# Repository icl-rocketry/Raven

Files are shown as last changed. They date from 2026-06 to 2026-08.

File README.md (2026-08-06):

# Project RAVEN

Solid-state particle detector for a rocket payload. Detects cosmic radiation
throughout flight and logs each hit with altitude, to build up counting
statistics post-flight.

Built in KiCad. Mixed-signal board: the detector board reads two independent
silicon-diode detector channels and logs events. 

## How it works 

A cosmic particle hits a reverse-biased photodiode and dumps a few femtocoulombs
of charge. A charge-sensitive amplifier turns that into a ~7 mV pulse, a
comparator checks it against a tunable threshold and the output signal is processed
by a seperate Pickle Rick board. Two diodes on two independent
channels double the sensitive area without doubling the noise.

## Repository layout

The KiCad project has five schematic sheets:
Using the ICLR Board Template

| Sheet | Contents |
|-------|----------|
| Root | status LEDs, connectors, test points |
| Power Board | Three isolated rails off a ~7.4V battery: +25V bias, +5V analogue, +3.3V digital |
| Detector Board | The signal chain: diodes, charge amps, comparators (2 channels) |

## specs

- **Enclosure:** Circa 90 x 90 x 100 mm (TBD), light-tight detector housing
- **Power:** ~1.5 W from a ~7.4V battery (cell TBC)
- **Detector:** 2x BPW34 photodiodes, biased at +50V
- **Front-end:** ADA4817-1 charge amp, TLV3201 comparator, per channel
- **MCU:** ESP32-S3

## Status

Work in progress. Schematic of the detector front-end is nearly
complete; layout, bring-up, and firmware still to come.

**Outstanding before layout:**
- Confirm comparator edge polarity on the bench (rising vs falling) before
  writing interrupt firmware
- Clear all ERC

## Firmware

Firmware is set up for PlatformIO. Clone the repo and open in PlatformIO to
build and flash.

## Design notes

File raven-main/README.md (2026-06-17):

# Ricardo Board Template
This is a KiCad template including the required components for an ESP32S3 with a USB-C port, a CAN transceiver, as well as logic power input regulation. This is the bare minimum needed for boards in the ricardo ecosystem. If you have followed the [hardware library usage instructions](https://github.com/icl-rocketry/iclr-hw), the hardware libraries will automatically be added to every project started from this template.

## Usage
To use this, clone this repository in your KiCad user templates folder.

By default, this folder is:

MacOS - ```/Users/{USERNAME}/Documents/KiCad/8.0/template/```

Windows -  ```%USERPROFILE%/Documents/KiCad/8.0/template```

Linux - ```/home/{USERNAME}/.local/share/kicad/8.0/template```

Then, you will be able to access the template when making a new project in ```KiCad -> File -> New Project from Template... -> User Templates```

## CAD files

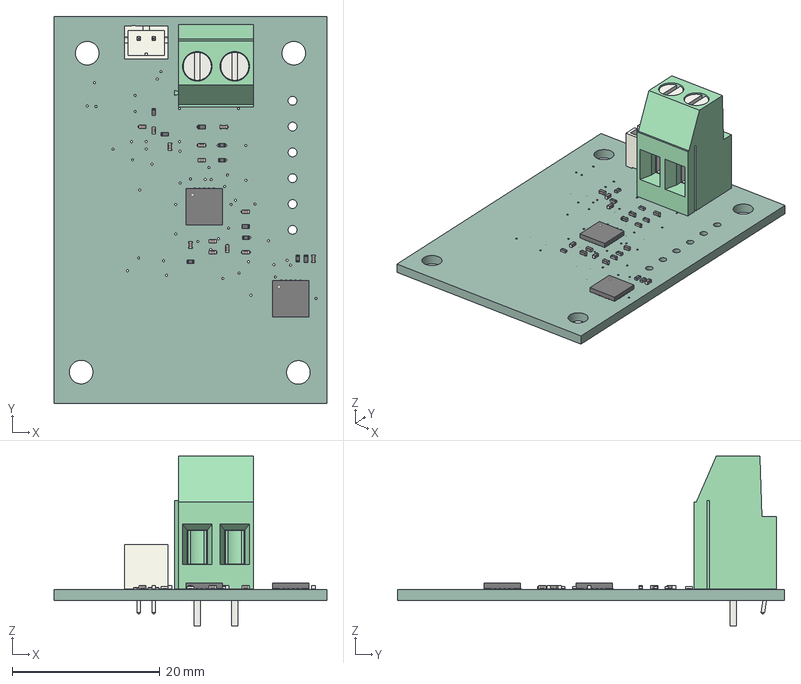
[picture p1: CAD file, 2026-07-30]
raven-main/Detector-Power-Board/Detector-Power-Board/PowerBoard.step
37.0 x 52.5 x 23.0 mm
C_0402_1005Metric x 13
R_0402_1005Metric x 10
Texas_RGW0020A_VQFN-20-1EP_5x5mm_P0.65mm_EP3.15x3.15mm x 2
JST_B2B_PH_K
TerminalBlock_Phoenix_MKDS-3-2-5.08_1x02_P5.08mm_Horizontal
det2136_PCB

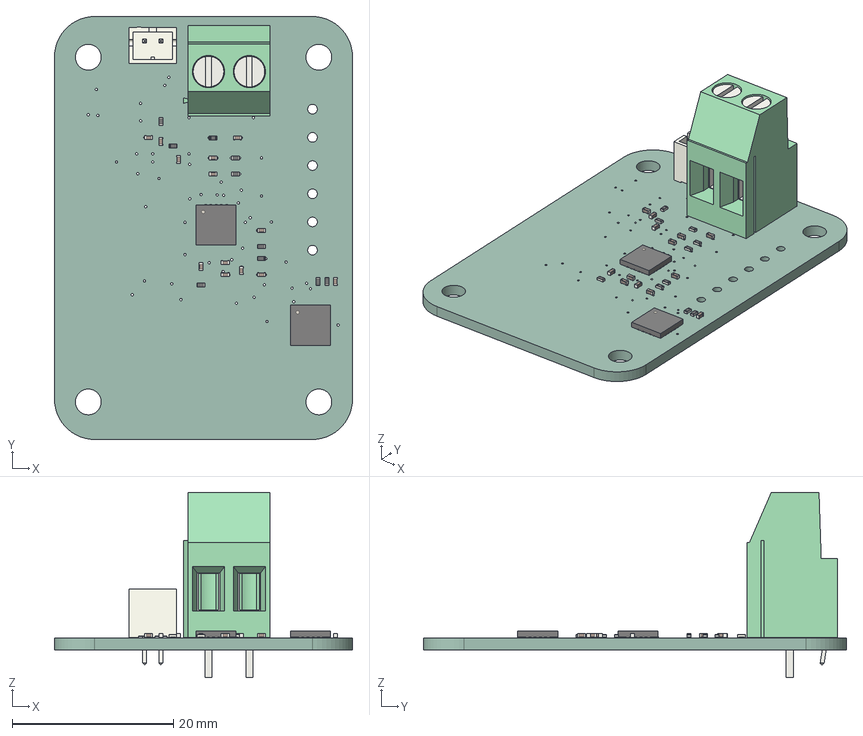
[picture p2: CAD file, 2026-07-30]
raven-main/Detector-Power-Board/PowerBoard(2).step
37.0 x 52.5 x 23.0 mm
C_0402_1005Metric x 13
R_0402_1005Metric x 10
Texas_RGW0020A_VQFN-20-1EP_5x5mm_P0.65mm_EP3.15x3.15mm x 2
JST_B2B_PH_K
TerminalBlock_Phoenix_MKDS-3-2-5.08_1x02_P5.08mm_Horizontal
detector-power_PCB

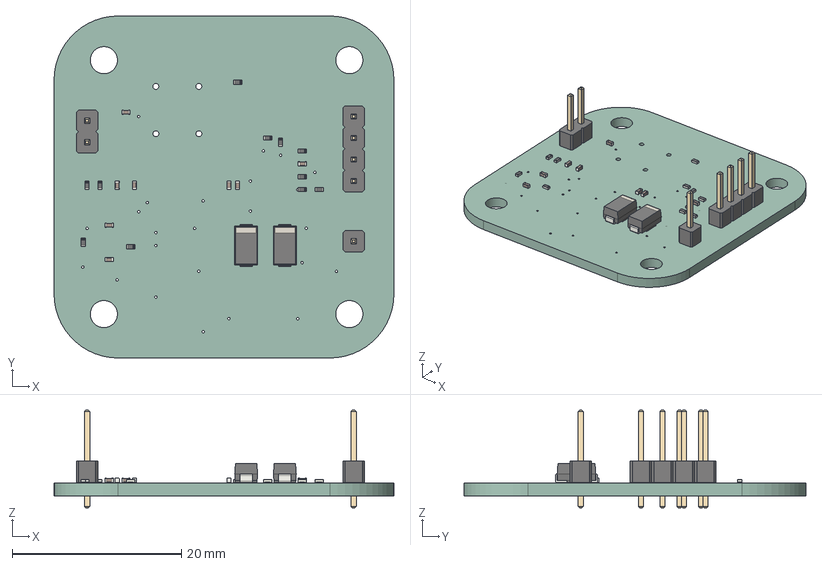
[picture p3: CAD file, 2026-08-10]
raven-main/Detector-Proto-Board/.step
40.2 x 40.4 x 11.5 mm
C_0402_1005Metric x 8
R_0402_1005Metric x 11
PinHeader_1x02_P254mm_Vertical
D_SMA x 2
PinHeader_1x01_P254mm_Vertical
PinHeader_1x04_P254mm_Vertical
Detector-Proto-Board_PCB

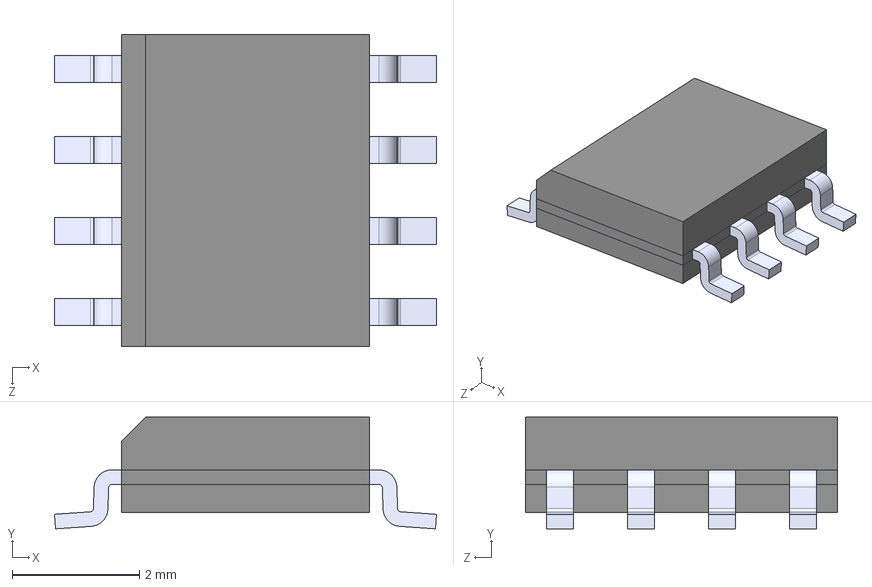
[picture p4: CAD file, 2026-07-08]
raven-main/Detector-Proto-Board/ADA4817-1ARDZ-R7/ADA4817-1ARDZ-R7.step
5.99 x 1.75 x 4.90 mm

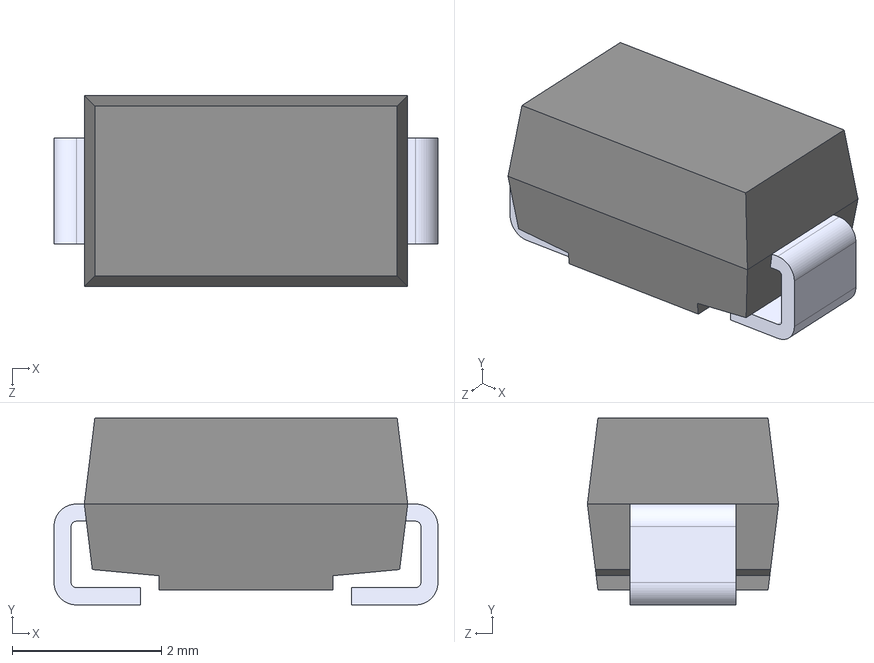
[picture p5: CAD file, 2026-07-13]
raven-main/Detector-Proto-Board/SMAJ5.0A/SMAJ5.0A.step
5.14 x 2.50 x 2.56 mm

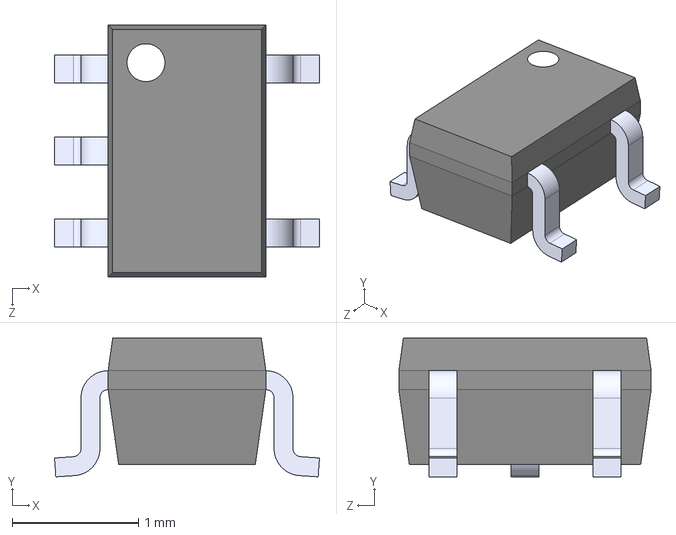
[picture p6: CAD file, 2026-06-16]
raven-main/Detector-Proto-Board/TLV3201AIDCKT/TLV3201AIDCKT.step
2.10 x 1.10 x 2.00 mm

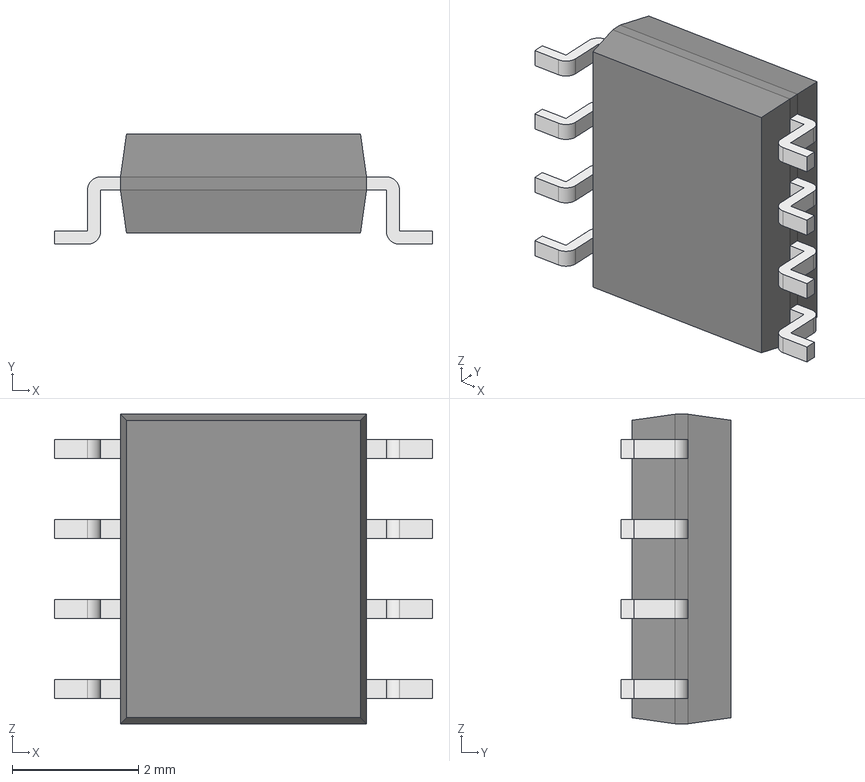
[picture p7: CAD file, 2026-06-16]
raven-main/OPA656UB/OPA656UB.step
5.99 x 1.75 x 4.91 mm
Body001 (Mirror #1) x 4
XY-plane x 12
X-axis x 12

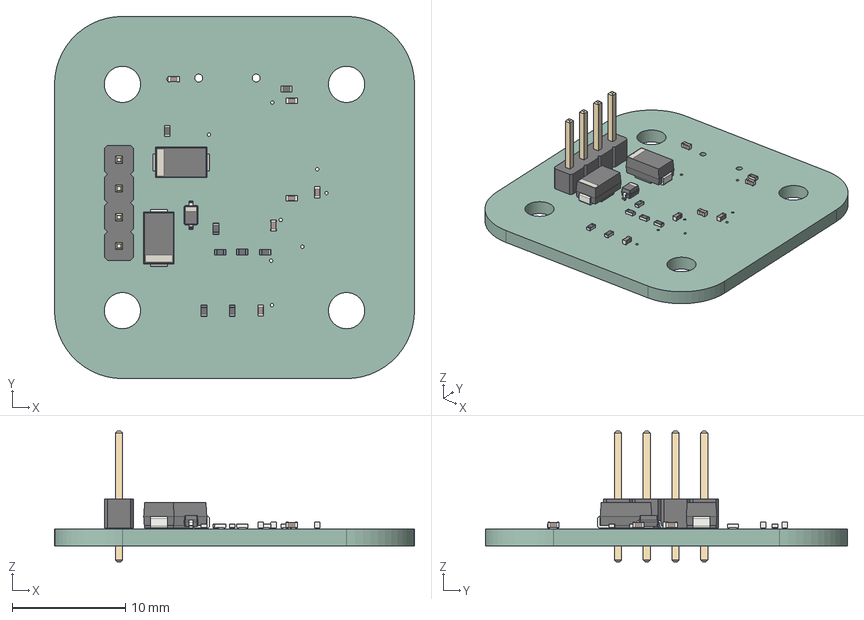
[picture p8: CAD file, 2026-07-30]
raven-main/Detector-Proto-Board/ProtoBoard.step
31.8 x 32.0 x 11.5 mm
R_0402_1005Metric x 8
C_0402_1005Metric x 6
PinHeader_1x04_P254mm_Vertical
D_SMA x 2
D_SOD-323
Detector-Proto-Board_PCB

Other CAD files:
raven-main/Detector-Proto-Board/Protoboard-v2.step
Raven Electronics Assembly.f3z

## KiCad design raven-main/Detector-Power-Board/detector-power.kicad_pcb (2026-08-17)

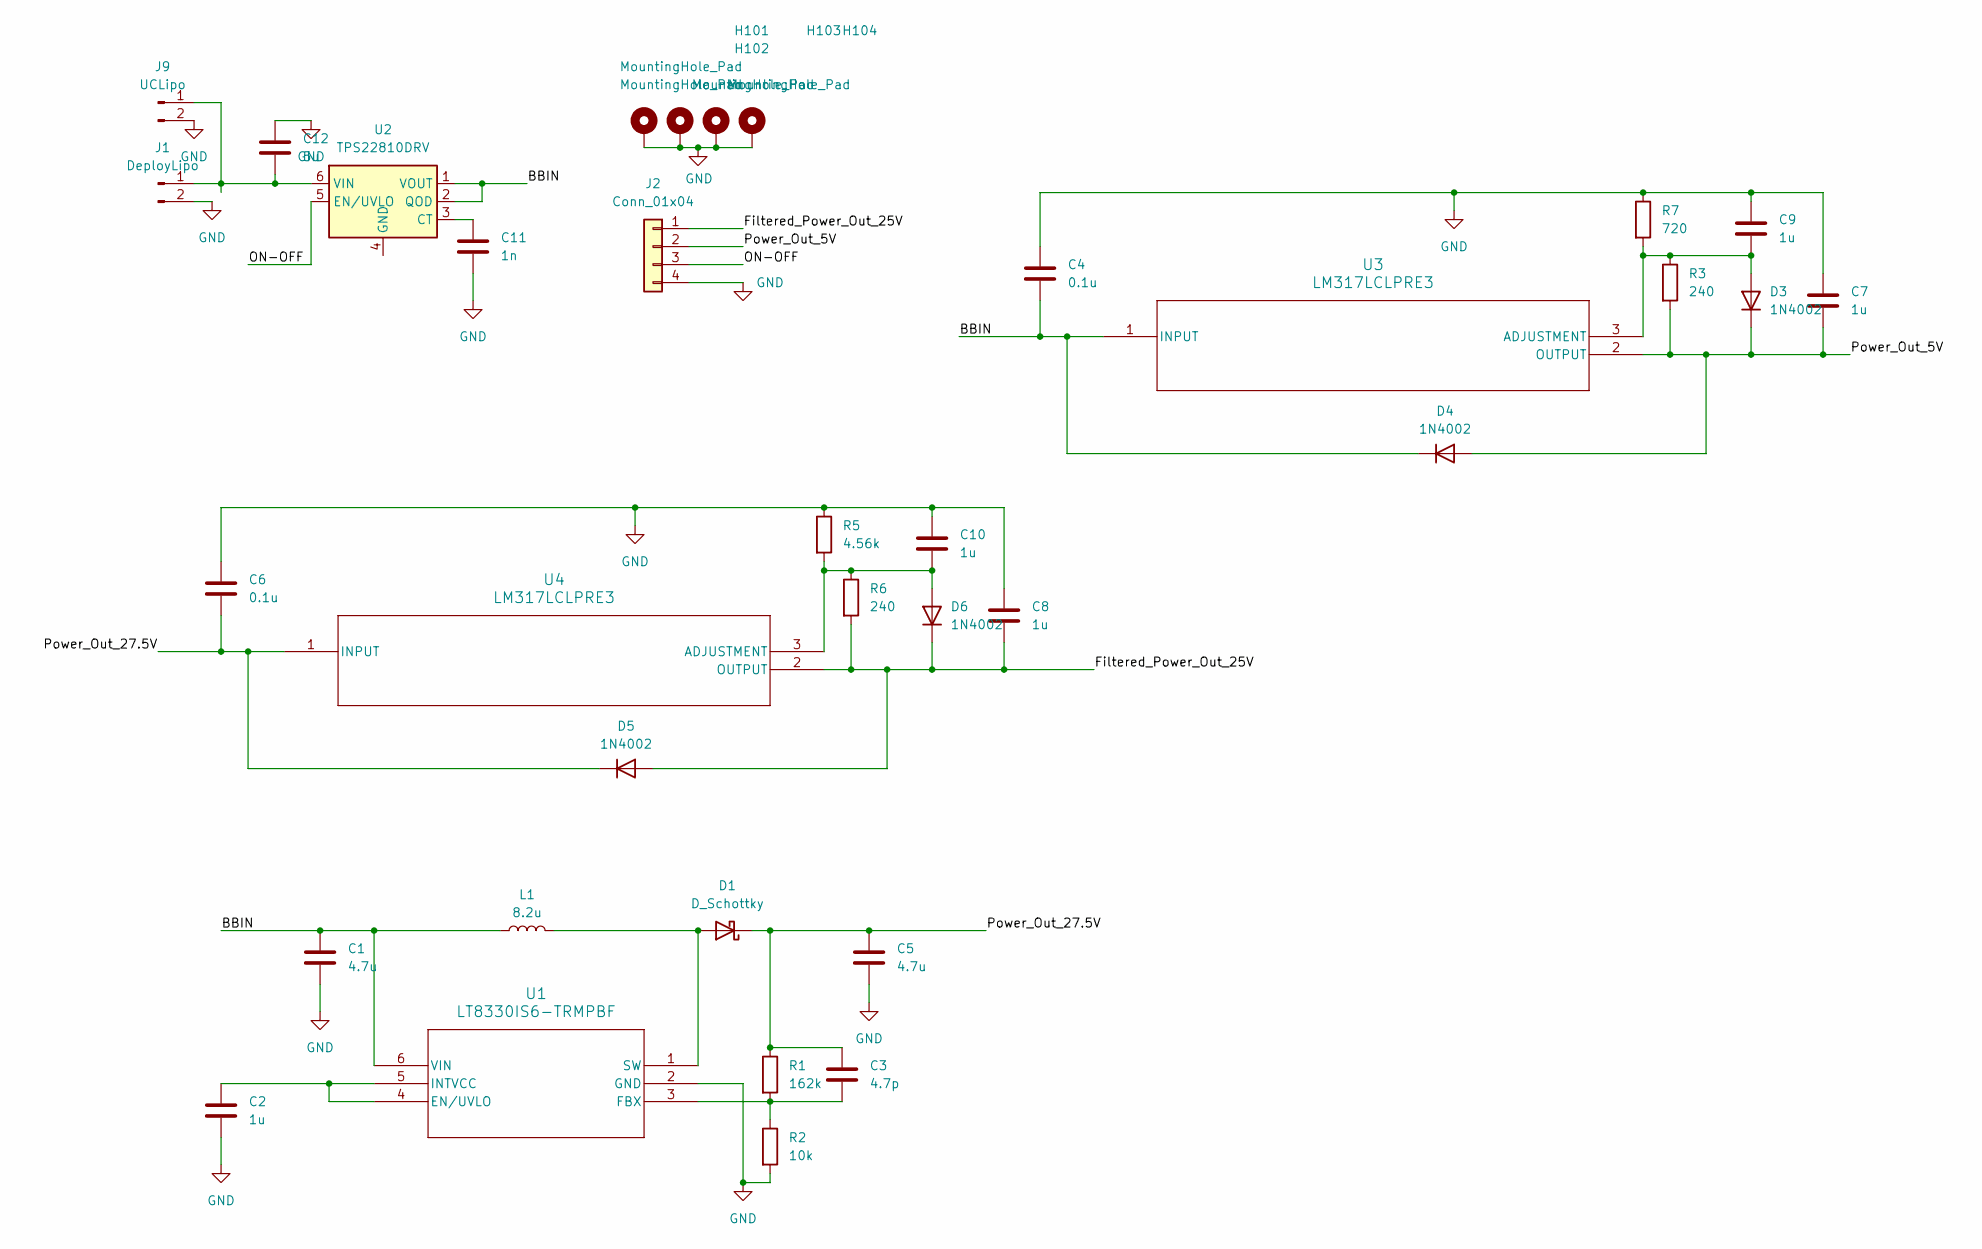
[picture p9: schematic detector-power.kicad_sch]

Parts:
C1, C5: 4.7u; C_0805_2012Metric
C2, C7, C8, C9, C10: 1u; C_0805_2012Metric
C3: 4.7p; C_0805_2012Metric
C4, C6: 0.1u; C_0805_2012Metric
C11: 1n; C_0805_2012Metric
C12: 5u; C_0805_2012Metric
D1: D_Schottky; SOD323F_NEX
D3, D4, D5, D6: 1N4002; D_DO-41_SOD81_P10.16mm_Horizontal
H101, H102, H103, H104: MountingHole_Pad; MountingHole_3.2mm_M3_DIN965_Pad
J1: DeployLipo; TerminalBlock_Phoenix_MKDS-3-2-5.08_1x02_P5.08mm_Horizontal
J2: Conn_01x04; PinHeader_1x04_P2.54mm_Vertical
J9: UCLipo; JST_PH_B2B-PH-K_1x02_P2.00mm_Vertical
L1: 8.2u; IND_8R0NC_SUM
R1: 162k; R_0402_1005Metric
R2: 10k; R_0402_1005Metric
R3, R6: 240; R_0402_1005Metric
R5: 4.56k; R_0402_1005Metric
R7: 720; R_0402_1005Metric
U1: LT8330IS6-TRMPBF; IC6_LT8330IS6-TRMPBF_ADI
U2: TPS22810DRV; WSON-6-1EP_2x2mm_P0.65mm_EP1x1.6mm
U3, U4: LM317LCLPRE3; TD03B_TEX

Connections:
/BBIN: C1.1, C4.2, D4.1 (K), L1.1, U1.6 (VIN), U2.1 (VOUT), U2.2 (QOD), U3.1 (INPUT)
/Filtered_Power_Out_25V: C8.2, D5.2 (A), D6.1 (K), J2.1, R6.2, U4.2 (OUTPUT)
/ON-OFF: J2.3, U2.5 (EN/UVLO)
/Power_Out_5V: C7.2, D3.1 (K), D4.2 (A), J2.2, R3.2, U3.2 (OUTPUT)
/Power_Out_27.5V: C3.1, C5.1, C6.2, D1.1 (K), D5.1 (K), R1.1, U4.1 (INPUT)
GND: C1.2, C2.2, C4.1, C5.2, C6.1, C7.1, C8.1, C9.1, C10.1, C11.2, C12.2, H101.1 (1_1), H102.1 (1_1), H103.1 (1_1), H104.1 (1_1), J1.2, J2.4, J9.2, R2.2, R5.1, R7.1, U1.2 (GND)
unnamed: D1.2 (A), L1.2, U1.1 (SW)
unnamed: C9.2, D3.2 (A), R3.1, R7.2, U3.3 (ADJUSTMENT)
unnamed: C10.2, D6.2 (A), R5.2, R6.1, U4.3 (ADJUSTMENT)
unnamed: C12.1, J1.1, J9.1, U2.6 (VIN)
unnamed: C2.1, U1.4 (EN/UVLO), U1.5 (INTVCC)
unnamed: C3.2, R1.2, R2.1, U1.3 (FBX)
unnamed: C11.1, U2.3 (CT)
unnamed: U2.4 (GND), U2.7 (GND)

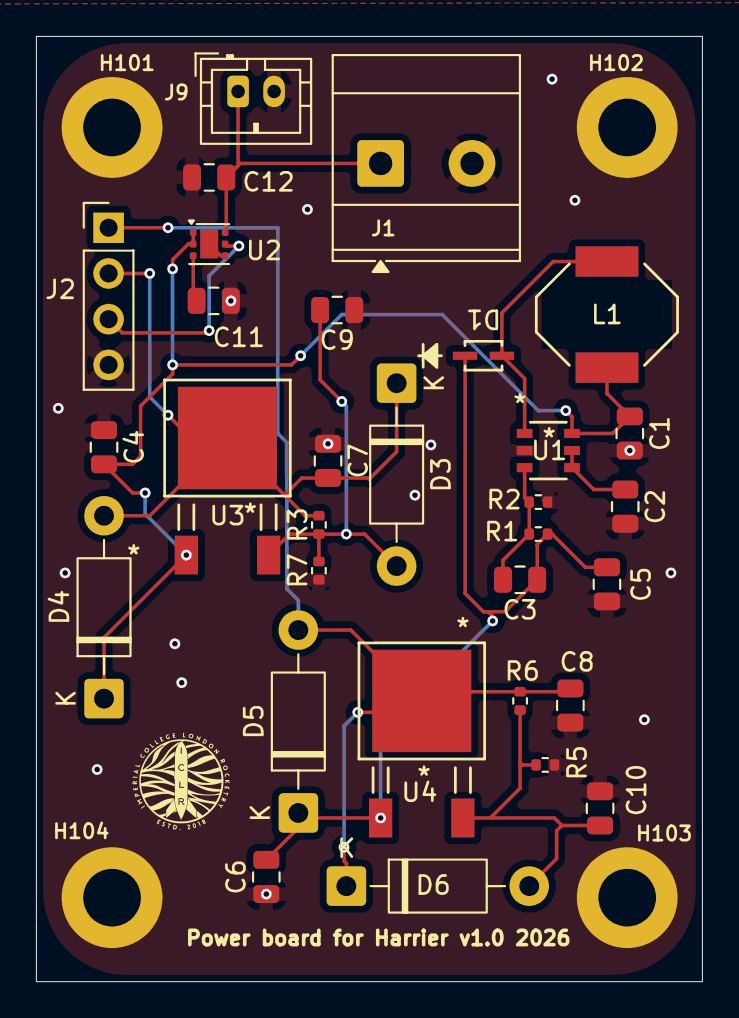
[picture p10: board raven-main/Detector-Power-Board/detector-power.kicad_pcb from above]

Board: 2 copper layers, 37.0 x 52.5 mm, 35 parts (0 on the bottom side), 14 nets.

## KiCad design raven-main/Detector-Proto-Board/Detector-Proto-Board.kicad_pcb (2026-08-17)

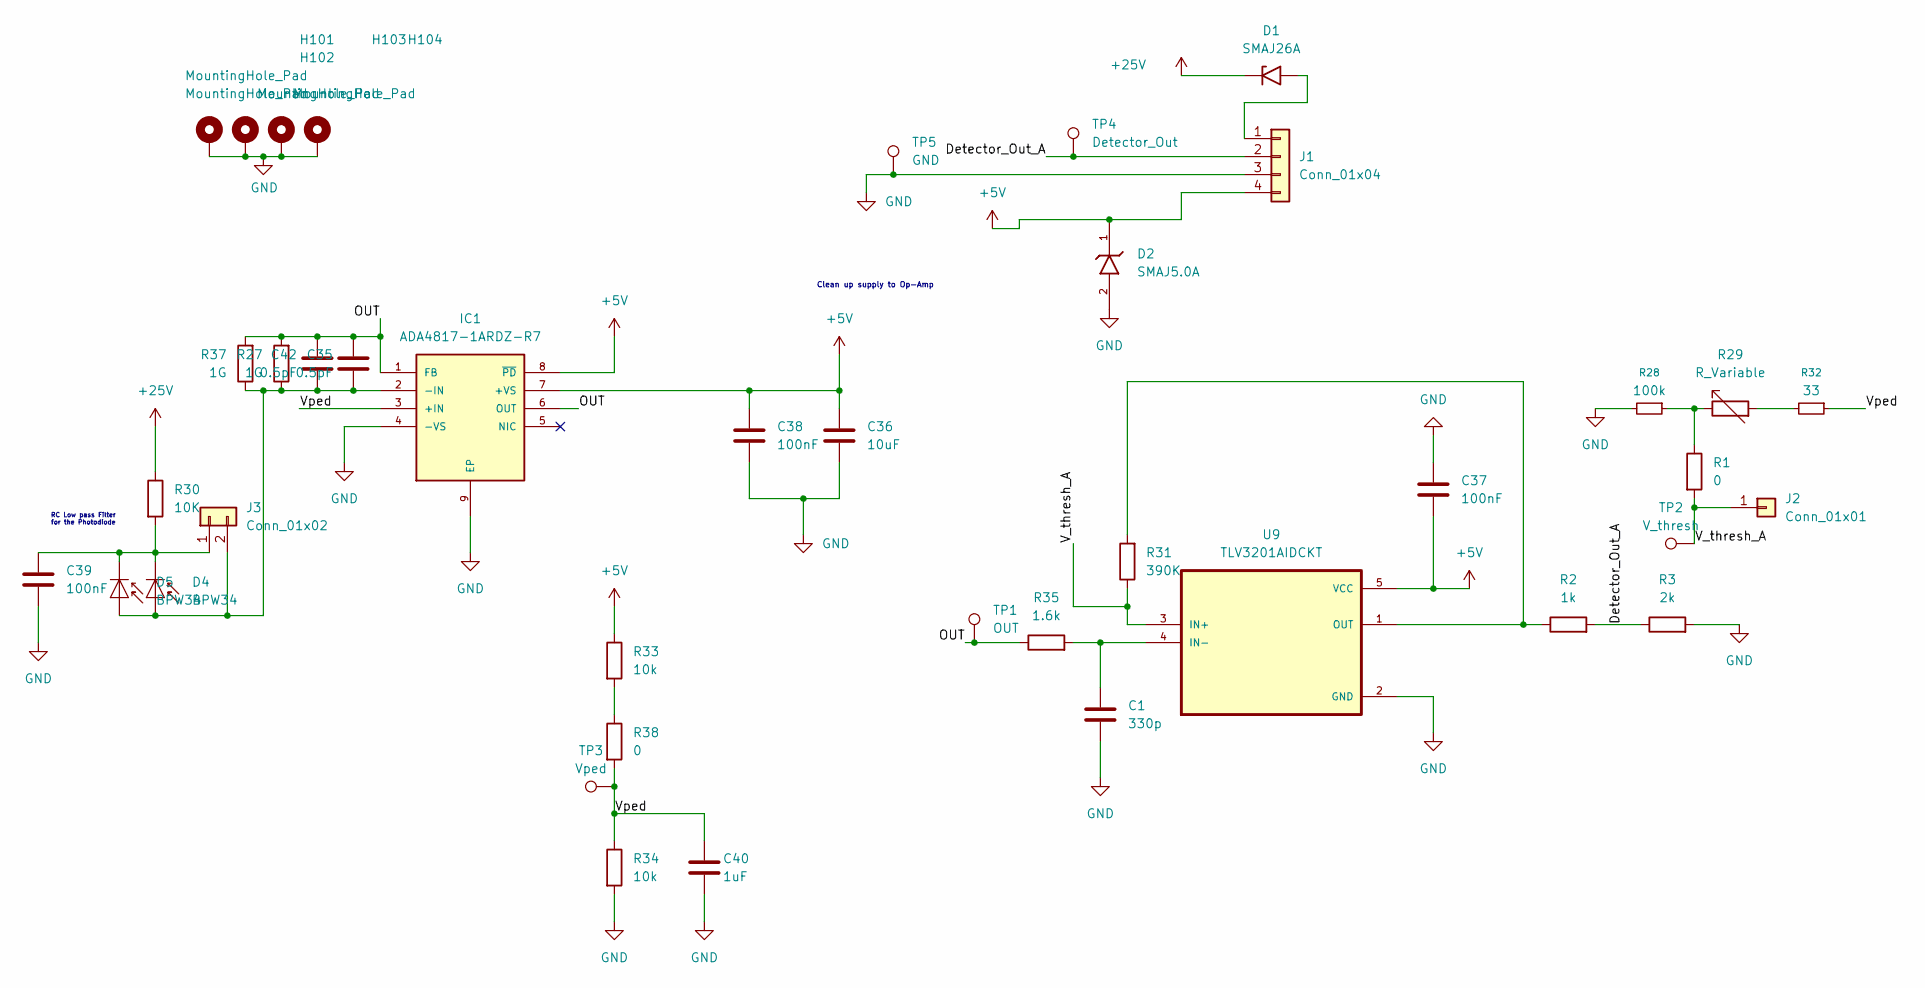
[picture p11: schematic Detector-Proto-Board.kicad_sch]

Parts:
C1: 330p; C_0402_1005Metric
C35, C42: 0.5pF; C_0402_1005Metric
C36: 10uF; C_0402_1005Metric
C37, C38, C39: 100nF; C_0402_1005Metric
C40: 1uF; C_0402_1005Metric
D1: SMAJ26A; D_SMA
D2: SMAJ5.0A; D_SMA; MOUSER_PART_NUMBER 576-SMAJ5.0A
D4, D5: BPW34; Osram_DIL2_4.3x4.65mm_P5.08mm
H101, H102, H103, H104: MountingHole_Pad; MountingHole_3.2mm_M3_DIN965_Pad
IC1: ADA4817-1ARDZ-R7; SOIC127P600X175-9N; Mouser_Part_Number 584-ADA4817-1ARDZ-R7
J1: Conn_01x04; PinHeader_1x04_P2.54mm_Vertical
J2: Conn_01x01; PinHeader_1x01_P2.54mm_Vertical
J3: Conn_01x02; PinHeader_1x02_P2.54mm_Vertical
R1, R38: 0; R_0402_1005Metric
R2: 1k; R_0402_1005Metric
R3: 2k; R_0402_1005Metric
R27, R37: 1G; R_0402_1005Metric
R28: 100k; R_0402_1005Metric
R29: R_Variable; SOT_502E
R30: 10K; R_0402_1005Metric
R31: 390K; R_0402_1005Metric
R32: 33; R_0402_1005Metric
R33, R34: 10k; R_0402_1005Metric
R35: 1.6k; R_0402_1005Metric
TP1: OUT; TestPoint_Pad_D2.5mm
TP2: V_thresh; TestPoint_Pad_D2.5mm
TP3: Vped; TestPoint_Pad_D2.5mm
TP4: Detector_Out; TestPoint_Pad_D2.5mm
TP5: GND; TestPoint_Pad_D2.5mm
U9: TLV3201AIDCKT; SOT65P210X110-5N

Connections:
+5V: C36.1, C37.2, C38.2, D2.1, IC1.7 (+VS), IC1.8 (~PD), J1.4, R33.1, U9.5 (VCC)
+25V: D1.1 (A1), R30.1
/Detector_Out_A: J1.2, R2.2, R3.1, TP4.1 (1_1)
/OUT: C35.2, C42.2, IC1.1 (FB), IC1.6 (OUT), R27.2, R35.1, R37.2, TP1.1 (1_1)
/V_thresh_A: J2.1 (Pin_1_1), R1.2, R31.1, TP2.1 (1_1), U9.3 (IN+)
/Vped: C40.1, IC1.3 (+IN), R32.1, R34.1, R38.2, TP3.1 (1_1)
GND: C1.2, C36.2, C37.1, C38.1, C39.2, C40.2, D2.2, H101.1 (1_1), H102.1 (1_1), H103.1 (1_1), H104.1 (1_1), IC1.4 (-VS), IC1.9 (EP), J1.3, R3.2, R28.2, R34.2, TP5.1 (1_1), U9.2 (GND)
unnamed: D1.2 (A2), J1.1
unnamed: C35.1, C42.1, D4.2 (A), D5.2 (A), IC1.2 (-IN), J3.2, R27.1, R37.1
unnamed: C39.1, D4.1 (K), D5.1 (K), J3.1, R30.2
unnamed: R1.1, R28.1, R29.1
unnamed: R29.2, R32.2
unnamed: R33.2, R38.1
unnamed: C1.1, R35.2, U9.4 (IN-)
unnamed: R2.1, R31.2, U9.1 (OUT)

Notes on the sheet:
Clean up supply to Op-Amp
RC Low pass Filter for the Photodiode

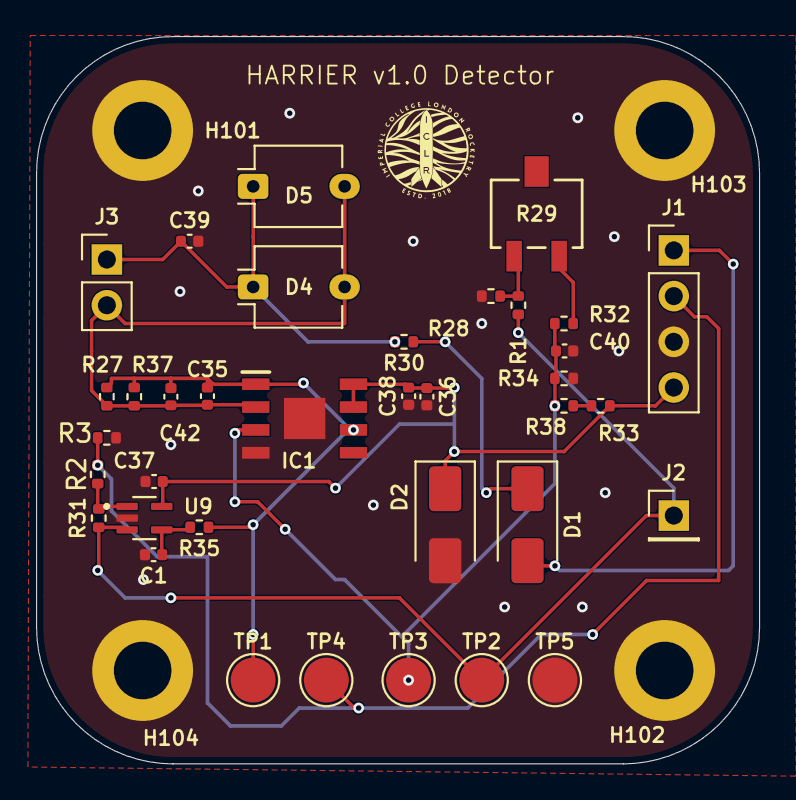
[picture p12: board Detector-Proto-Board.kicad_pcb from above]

Board: 2 copper layers, 40.2 x 40.4 mm, 40 parts (0 on the bottom side), 15 nets.

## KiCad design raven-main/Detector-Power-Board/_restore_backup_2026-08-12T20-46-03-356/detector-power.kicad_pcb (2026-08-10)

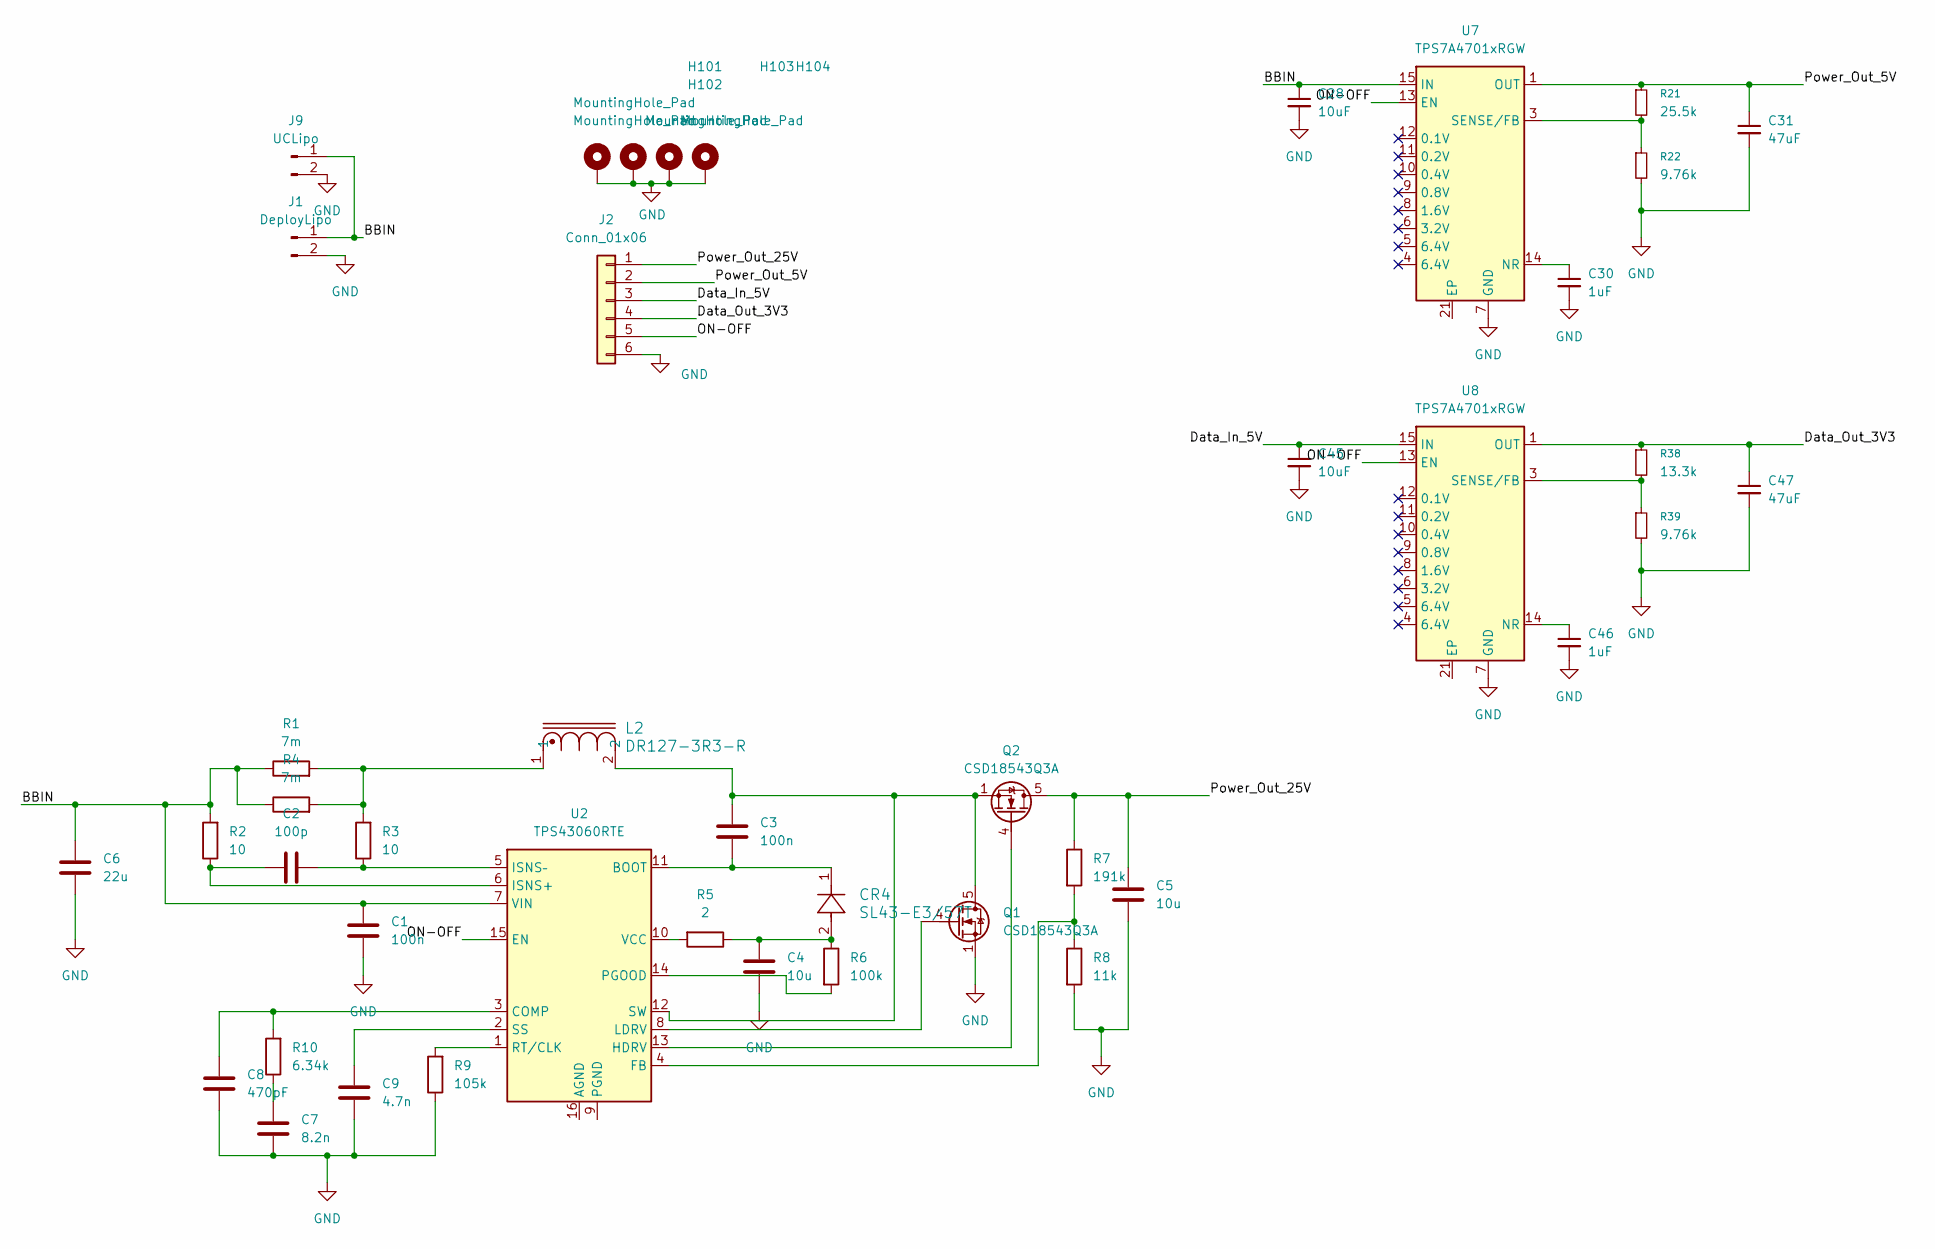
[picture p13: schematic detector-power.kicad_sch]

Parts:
C1, C3: 100n; C_0402_1005Metric
C2: 100p; C_0402_1005Metric
C4, C5: 10u; C_0402_1005Metric
C6: 22u; C_0402_1005Metric
C7: 8.2n; C_0402_1005Metric
C8: 470pF; C_0402_1005Metric
C9: 4.7n; C_0402_1005Metric
C28, C45: 10uF; C_0402_1005Metric
C30, C46: 1uF; C_0402_1005Metric
C31, C47: 47uF; C_0402_1005Metric
CR4: SL43-E3/57T; DIODE_DO214AB
H101, H102, H103, H104: MountingHole_Pad; MountingHole_3.2mm_M3_DIN965_Pad
J1: DeployLipo; TerminalBlock_Phoenix_MKDS-3-2-5.08_1x02_P5.08mm_Horizontal
J2: Conn_01x06; TerminalBlock_4Ucon_1x06_P3.50mm_Horizontal
J9: UCLipo; JST_PH_B2B-PH-K_1x02_P2.00mm_Vertical
L2: DR127-3R3-R; DR127
Q1, Q2: CSD18543Q3A; VSON-8_3.3x3.3mm_P0.65mm_NexFET
R1, R4: 7m; R_0402_1005Metric
R2, R3: 10; R_0402_1005Metric
R5: 2; R_0402_1005Metric
R6: 100k; R_0402_1005Metric
R7: 191k; R_0402_1005Metric
R8: 11k; R_0402_1005Metric
R9: 105k; R_0402_1005Metric
R10: 6.34k; R_0402_1005Metric
R21: 25.5k; R_0402_1005Metric
R22, R39: 9.76k; R_0402_1005Metric
R38: 13.3k; R_0402_1005Metric
U2: TPS43060RTE; Texas_RTE_WQFN-16-1EP_3x3mm_P0.5mm_EP1.2x0.8mm_ThermalVias
U7, U8: TPS7A4701xRGW; Texas_RGW0020A_VQFN-20-1EP_5x5mm_P0.65mm_EP3.15x3.15mm_Ther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

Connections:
/BBIN: C1.1, C6.1, C28.1, J1.1, J9.1, R1.1, R2.2, R4.1, U2.7 (VIN), U7.15 (IN), U7.16 (IN)
/Data_In_5V: C45.1, J2.3, U8.15 (IN), U8.16 (IN)
/Data_Out_3V3: C47.1, J2.4, R38.1, U8.1 (OUT), U8.20 (OUT)
/ON-OFF: J2.5, U2.15 (EN), U7.13 (EN), U8.13 (EN)
/Power_Out_5V: C31.1, J2.2, R21.1, U7.1 (OUT), U7.20 (OUT)
/Power_Out_25V: C5.1, J2.1, Q2.5 (D), R7.1
GND: C1.2, C4.2, C5.2, C6.2, C7.2, C8.2, C9.2, C28.2, C30.2, C31.2, C45.2, C46.2, C47.2, H101.1 (1_1), H102.1 (1_1), H103.1 (1_1), H104.1 (1_1), J1.2, J2.6, J9.2, Q1.1 (S), Q1.2 (S), Q1.3 (S), R8.2, R9.1, R22.2, R39.2, U7.7 (GND), U8.7 (GND)
unnamed: C4.1, CR4.2, R5.1, R6.1
unnamed: C7.1, R10.1
unnamed: L2.1, R1.2, R3.2, R4.2
unnamed: C3.1, L2.2, Q1.5 (D), Q2.1 (S), Q2.2 (S), Q2.3 (S), U2.12 (SW)
unnamed: Q1.4 (G), U2.8 (LDRV)
unnamed: Q2.4 (G), U2.13 (HDRV)
unnamed: U2.16 (AGND), U2.17 (AGND)
unnamed: C3.2, CR4.1, U2.11 (BOOT)
unnamed: C8.1, R10.2, U2.3 (COMP)
unnamed: R7.2, R8.1, U2.4 (FB)
unnamed: C2.1, R2.1, U2.6 (ISNS+)
unnamed: C2.2, R3.1, U2.5 (ISNS–)
unnamed: R6.2, U2.14 (PGOOD)
unnamed: R9.2, U2.1 (RT/CLK)
unnamed: C9.1, U2.2 (SS)
unnamed: R5.2, U2.10 (VCC)
unnamed: C30.1, U7.14 (NR)
unnamed: R21.2, R22.1, U7.3 (SENSE/FB)
unnamed: C46.1, U8.14 (NR)
unnamed: R38.2, R39.1, U8.3 (SENSE/FB)

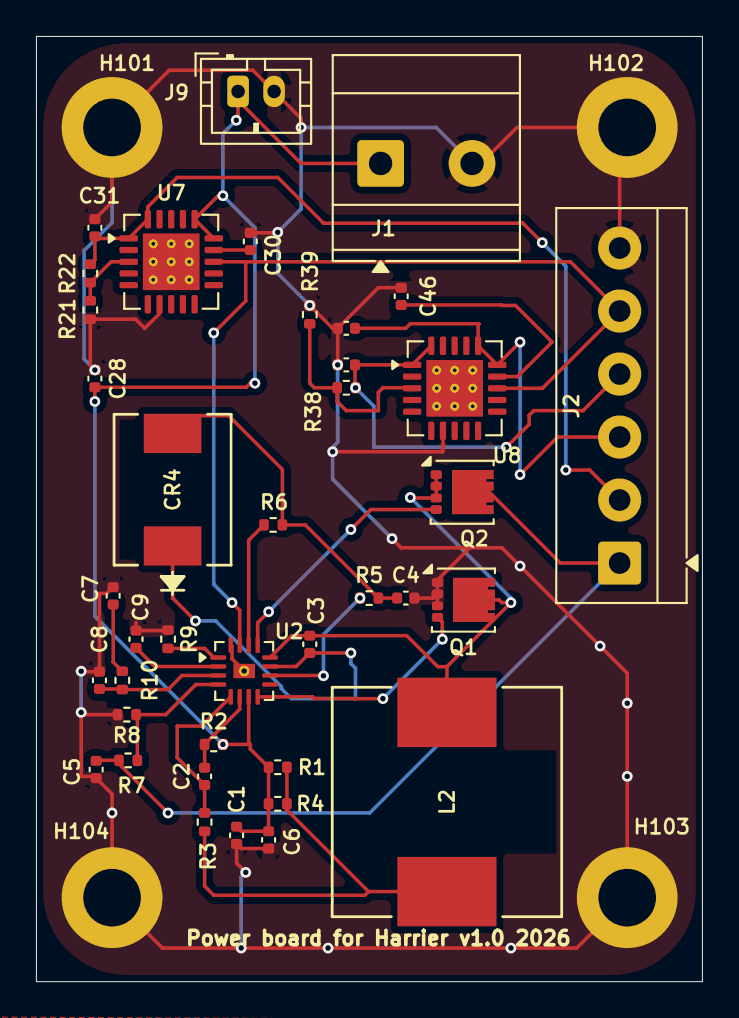
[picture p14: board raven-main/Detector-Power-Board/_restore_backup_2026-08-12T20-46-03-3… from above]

Board: 2 copper layers, 37.0 x 52.5 mm, 43 parts (0 on the bottom side), 27 nets.

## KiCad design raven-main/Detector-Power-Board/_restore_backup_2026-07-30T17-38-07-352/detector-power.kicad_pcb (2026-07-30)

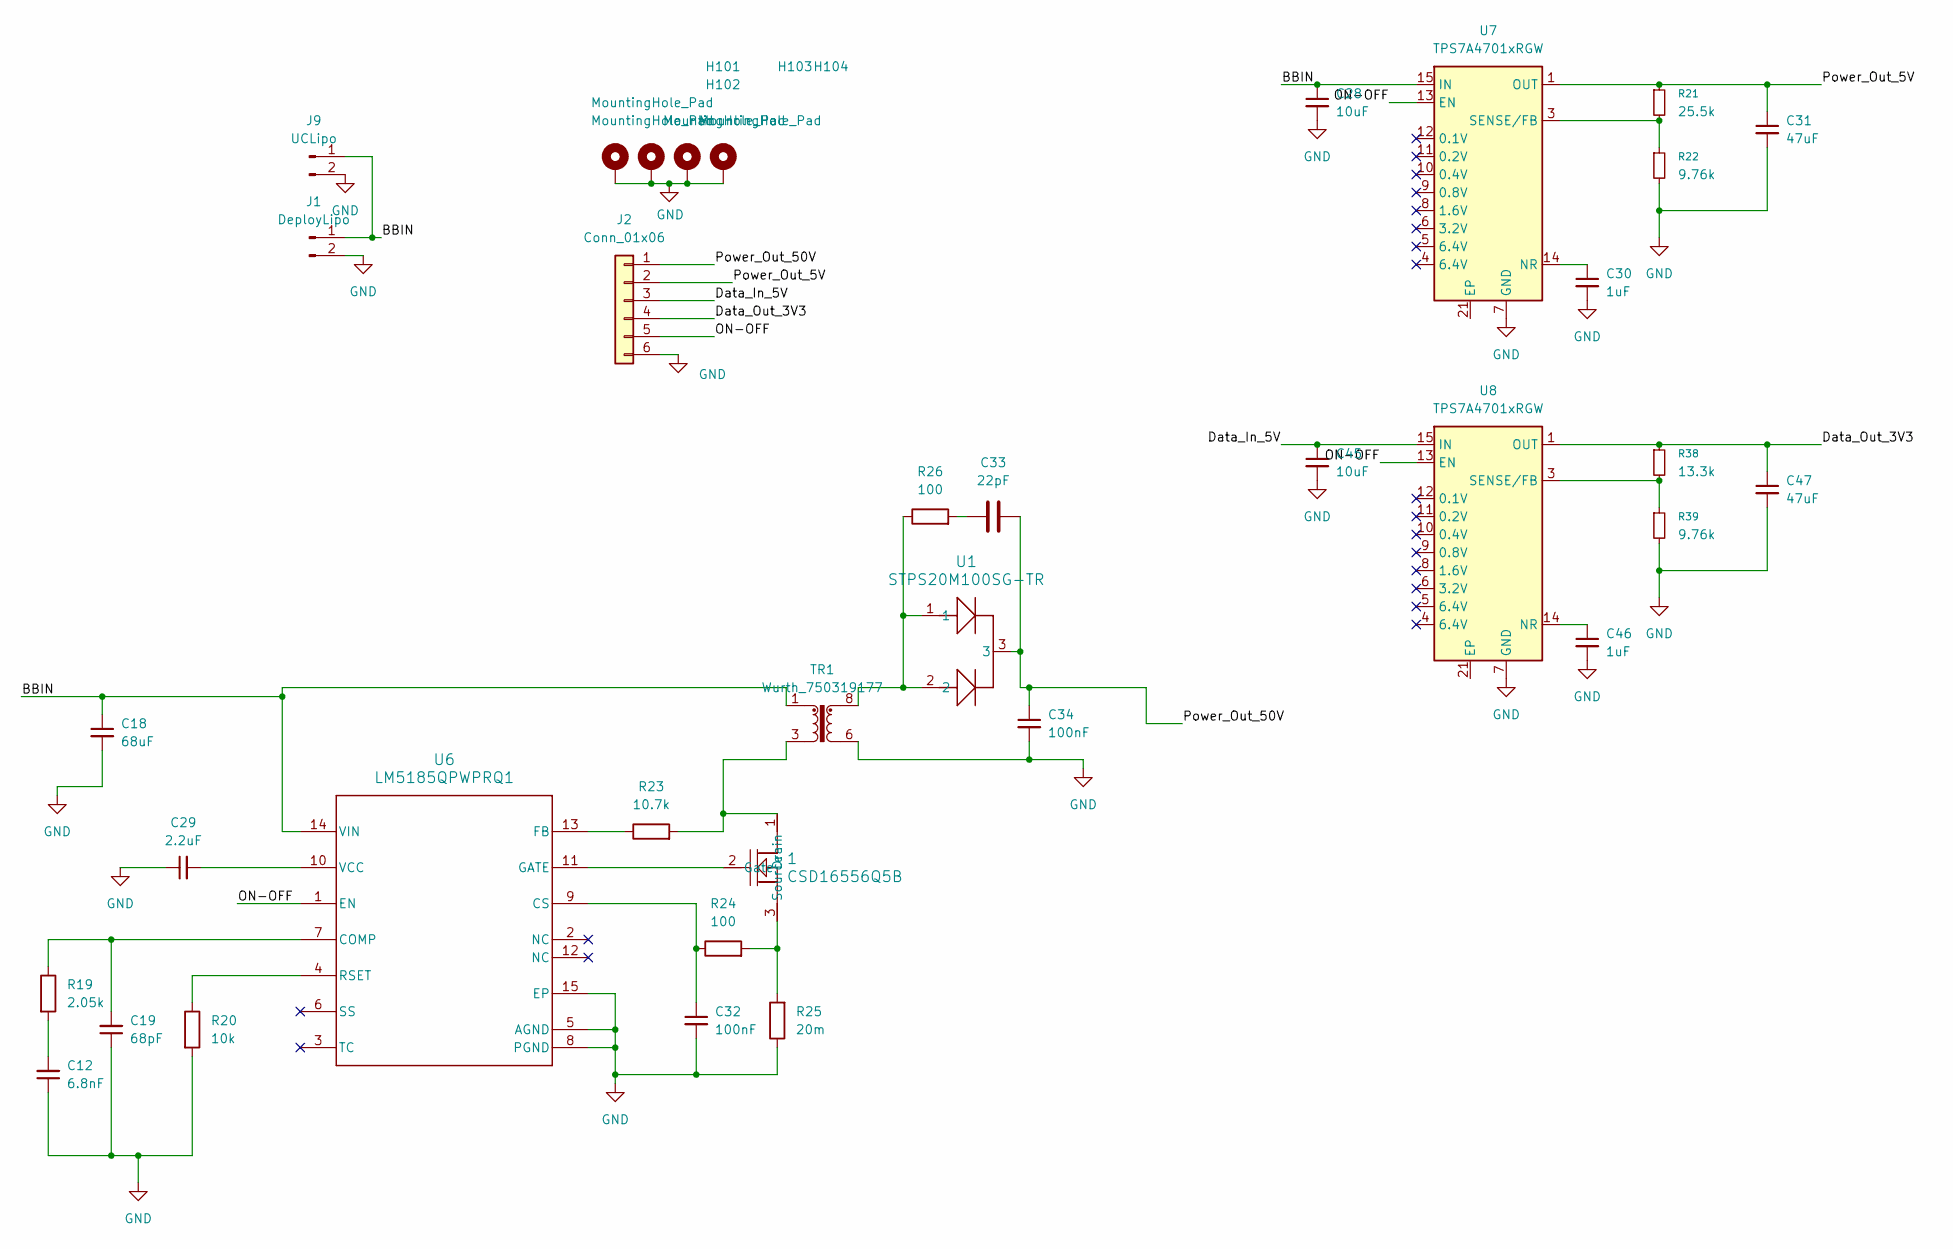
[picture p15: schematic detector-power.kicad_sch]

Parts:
1: CSD16556Q5B; DNK0008A
C12: 6.8nF; C_0402_1005Metric
C18: 68uF; C_0402_1005Metric
C19: 68pF; C_0402_1005Metric
C28, C45: 10uF; C_0402_1005Metric
C29: 2.2uF; C_0402_1005Metric
C30, C46: 1uF; C_0402_1005Metric
C31, C47: 47uF; C_0402_1005Metric
C32, C34: 100nF; C_0402_1005Metric
C33: 22pF; C_0402_1005Metric
H101, H102, H103, H104: MountingHole_Pad; MountingHole_3.2mm_M3_DIN965_Pad
J1: DeployLipo; TerminalBlock_Phoenix_MKDS-3-2-5.08_1x02_P5.08mm_Horizontal
J2: Conn_01x06; TerminalBlock_4Ucon_1x06_P3.50mm_Horizontal
J9: UCLipo; JST_PH_B2B-PH-K_1x02_P2.00mm_Vertical
R19: 2.05k; R_0402_1005Metric
R20: 10k; R_0402_1005Metric
R21: 25.5k; R_0402_1005Metric
R22, R39: 9.76k; R_0402_1005Metric
R23: 10.7k; R_0402_1005Metric
R24, R26: 100; R_0402_1005Metric
R25: 20m; R_0402_1005Metric
R38: 13.3k; R_0402_1005Metric
TR1: Wurth_750319177; Transformer_Wurth_WE-AGDT-EP7
U1: STPS20M100SG-TR; D2PAK_STM
U6: LM5185QPWPRQ1; PWP0014G-IPC_A
U7, U8: TPS7A4701xRGW; Texas_RGW0020A_VQFN-20-1EP_5x5mm_P0.65mm_EP3.15x3.15mm_Ther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

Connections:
/BBIN: C18.1, C28.1, J1.1, J9.1, TR1.1, U6.14 (VIN), U7.15 (IN), U7.16 (IN)
/Data_In_5V: C45.1, J2.3, U8.15 (IN), U8.16 (IN)
/Data_Out_3V3: C47.1, J2.4, R38.1, U8.1 (OUT), U8.20 (OUT)
/ON-OFF: J2.5, U6.1 (EN), U7.13 (EN), U8.13 (EN)
/Power_Out_5V: C31.1, J2.2, R21.1, U7.1 (OUT), U7.20 (OUT)
/Power_Out_50V: C33.2, C34.1, J2.1, U1.3
GND: C12.1, C18.2, C19.1, C28.2, C29.1, C30.2, C31.2, C32.2, C34.2, C45.2, C46.2, C47.2, H101.1 (1_1), H102.1 (1_1), H103.1 (1_1), H104.1 (1_1), J1.2, J2.6, J9.2, R20.2, R22.2, R25.1, R39.2, TR1.6, U6.5 (AGND), U6.8 (PGND), U6.15 (EP), U7.7 (GND), U8.7 (GND)
unnamed: 1.1 (Drain), R23.2, TR1.3
unnamed: 1.2 (Gate), U6.11 (GATE)
unnamed: 1.3 (Source), R24.2, R25.2
unnamed: C12.2, R19.2
unnamed: C33.1, R26.2
unnamed: R26.1, TR1.8, U1.1, U1.2
unnamed: C19.2, R19.1, U6.7 (COMP)
unnamed: C32.1, R24.1, U6.9 (CS)
unnamed: R23.1, U6.13 (FB)
unnamed: R20.1, U6.4 (RSET)
unnamed: C29.2, U6.10 (VCC)
unnamed: C30.1, U7.14 (NR)
unnamed: R21.2, R22.1, U7.3 (SENSE/FB)
unnamed: C46.1, U8.14 (NR)
unnamed: R38.2, R39.1, U8.3 (SENSE/FB)

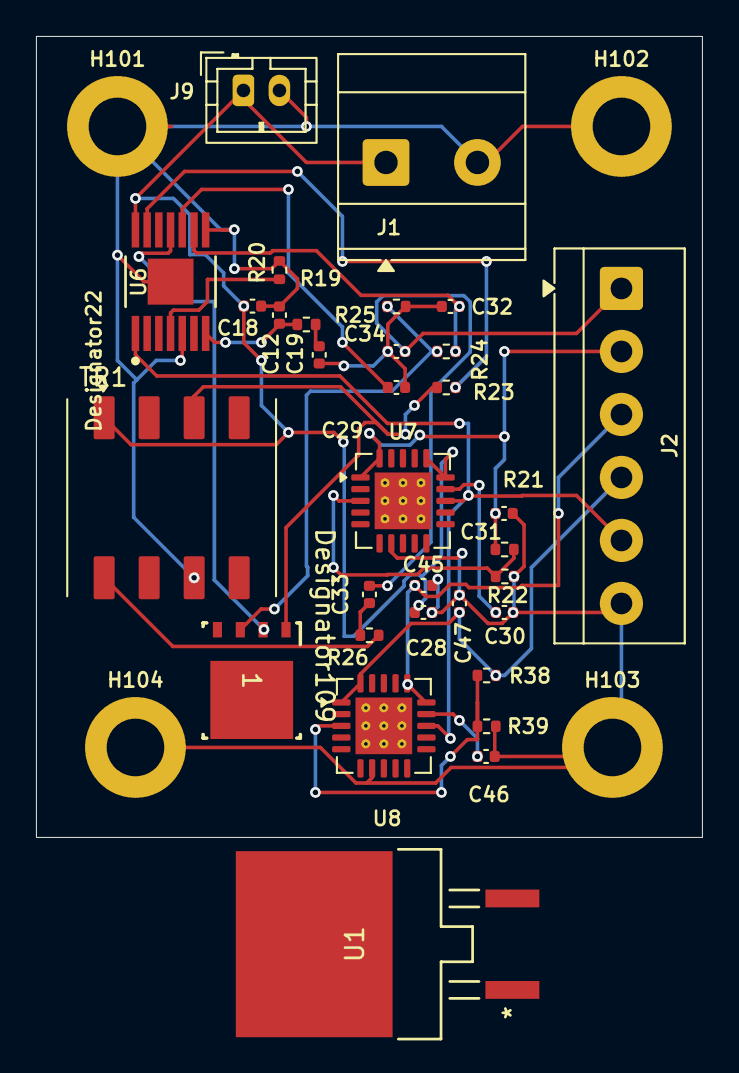
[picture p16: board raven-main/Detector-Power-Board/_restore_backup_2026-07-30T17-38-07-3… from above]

Board: 2 copper layers, 37.0 x 44.5 mm, 36 parts (0 on the bottom side), 22 nets.

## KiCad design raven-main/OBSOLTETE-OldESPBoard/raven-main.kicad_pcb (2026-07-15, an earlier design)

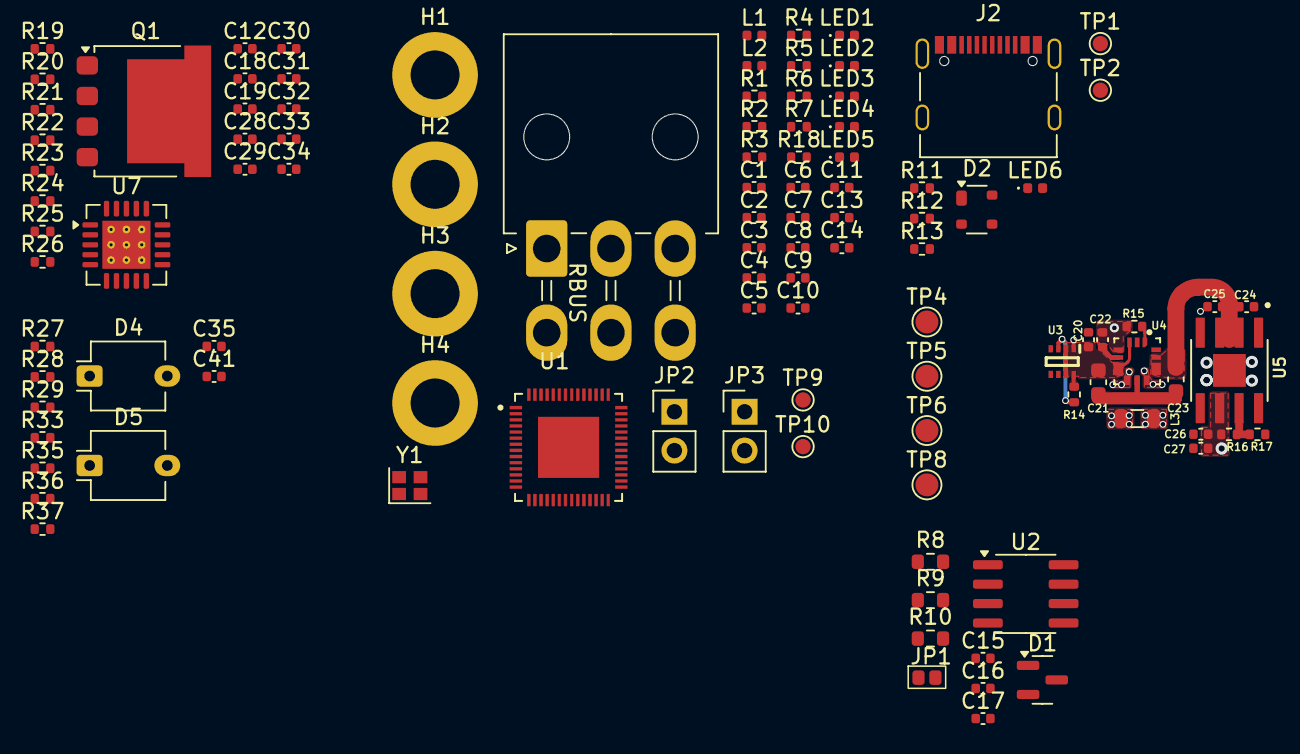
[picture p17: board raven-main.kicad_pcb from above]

Board: 4 copper layers, 107 parts (0 on the bottom side), 53 nets.

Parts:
C1, C16, C20, C24, C26, C28: 10uF; C_0402_1005Metric
C2, C4, C7, C22, C30: 1uF; C_0402_1005Metric
C3, C5, C6, C8, C10, C11, C27: 0.1uF; C_0402_1005Metric
C9: 10nF; C_0402_1005Metric
C12: 6.8nF; C_0402_1005Metric
C13, C14: 11pF; C_0402_1005Metric
C15, C32, C34: 100nF; C_0402_1005Metric
C17: 47nF; C_0402_1005Metric
C18: 68uF; C_0402_1005Metric
C19: 68pF; C_0402_1005Metric
C21: 10uF; C_0603_1608Metric
C23: 22uF; C_0603_1608Metric
C25: 4.7uF; C_0402_1005Metric
C29: 2.2uF; C_0402_1005Metric
C31: 47uF; C_0402_1005Metric
C33: 22pF; C_0402_1005Metric
C35, C41: 0.5pF; C_0402_1005Metric
D1: SM712_SOT23; SOT-23
D2: SP0503BAHT; SOT-143
D4, D5: BPW34; Osram_DIL2_4.3x4.65mm_P5.08mm
H1, H2, H3, H4: MountingHole_Pad; MountingHole_3.2mm_M3_DIN965_Pad
J1: RBUS; Molex_Mini-Fit_Jr_5569-06A2_2x03_P4.20mm_Horizontal
J2: USB_C_Receptacle_USB2.0; USB_C_Receptacle_Palconn_UTC16-G
JP1: TermJP; SmallerSolderJP
JP2, JP3: Conn_01x02_Male; PinHeader_1x02_P2.54mm_Vertical
L1: 2.0nH; L_0402_1005Metric
L2: 20nH; L_0402_1005Metric
L3: 1uH; L_0805_2012Metric
LED1, LED2: GREEN_LED; LED_0402_1005Metric
LED3: ORANGE_LED; LED_0402_1005Metric
LED4: BLUE_LED; LED_0402_1005Metric
LED5: RED_LED; LED_0402_1005Metric
LED6: WHITE_LED; LED_0402_1005Metric
Q1: SQJQ100EL; LFPAK88
R1, R3: 10K; R_0402_1005Metric
R2, R4: 470; R_0402_1005Metric
R5, R18: 1k; R_0402_1005Metric
R6: 499R; R_0402_1005Metric
R7: 3k; R_0402_1005Metric
R8: 0; R_0603_1608Metric
R9, R10: 60; R_0603_1608Metric
R11, R12, R13: 5.1k; R_0402_1005Metric
R14, R17, R20, R22: 10k; R_0402_1005Metric
R15: 14k; R_0402_1005Metric
R16: 56k; R_0402_1005Metric
R19: 2.05k; R_0402_1005Metric
R21: 25.5k; R_0402_1005Metric
R23: 10.7k; R_0402_1005Metric
R24, R26: 100; R_0402_1005Metric
R25: 20m; R_0402_1005Metric
R27, R33: 1G; R_0402_1005Metric
R28, R35: 100k; R_0402_1005Metric
R29, R36: R_Variable; R_0402_1005Metric
R37: 200; R_0402_1005Metric
TP1, TP2, TP9, TP10: TestPoint; TestPoint_Pad_D1.0mm
TP4, TP5, TP6, TP8: TestPoint; TestPoint_Pad_D1.5mm
U1: ESP32-S3; QFN40P700X700X90-57N
U2: SN65HVD230; SOIC-8_3.9x4.9mm_P1.27mm
U3: LM66200DRLR; SOTFL50P160X60-8N
U4: MAX77827AEFD+T; CONV_MAX77827AEFD+T
U5: SC4215ASTRT; SOIC127P599X175-9N
U7: TPS7A4701xRGW; Texas_RGW0020A_VQFN-20-1EP_5x5mm_P0.65mm_EP3.15x3.15mm_Ther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
Y1: R940000171; Crystal_SMD_2016-4Pin_2.0x1.6mm

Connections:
+3V3: C1.1, C4.1, C5.1, C7.1, C9.1, C10.1, C11.1, C15.1, C16.1, C26.2, C27.2, L1.1, R1.1, R2.1, R3.1, R4.2, R5.1, R16.1, R18.1, TP6.1 (1_1), U1.20 (VDD3P3_RTC), U1.46 (VDD3P3_CPU), U1.55 (VDDA), U1.56 (VDDA), U2.3 (VCC), U5.6 (VOUT)
+5V: C31.1, R21.1, R28.2, R35.2, U7.1 (OUT), U7.20 (OUT)
+50V: C1.2, C2.2, C3.2, C4.2, C5.2, C6.2, C7.2, C8.2, C9.2, C10.2, C11.2, C12.1, C13.2, C14.2, C15.2, C16.2, C17.2, C18.1, C18.2, C19.1, C20.1, C20.2, C21.1, C21.2, C22.2, C23.2, C24.2, C25.2, C26.1, C27.1, C28.1, C28.2, C29.1, C30.2, C31.2, C32.2, C33.2, C34.1, C34.2, D1.3 (common), D2.1 (A), H1.1 (1_1), H2.1 (1_1), H3.1 (1_1), H4.1 (1_1), J1.1, J1.2, J2.A1 (GND), J2.A12 (GND), J2.B1 (GND), J2.B12 (GND), J2.S1 (SHIELD), JP2.2, JP3.2, LED4.1 (K), LED5.1 (K), LED6.1 (K), R8.2, R11.2, R12.1, R15.2, R17.2, R20.2, R22.2, R25.1, R36.2, R37.1, TP4.1 (1_1), U1.57 (GND), U2.2 (GND), U3.1 (GND_1), U3.2 (VOUT_1), U3.4 (~ON), U3.5 (GND_2), U3.7 (VOUT_2), U4.3 (EN), U4.4 (AGND), U4.6 (IN), U4.9 (PGND), U5.8 (GND), U5.9 (GND), U7.7 (GND), U7.13 (EN), U7.15 (IN), U7.16 (IN), Y1.2, Y1.4
/BOOT: C8.1, JP3.1, R3.2, U1.5 (GPIO0/BOOT)
/CAN+: D1.2 (A2), J1.5, R9.1, U2.7 (CANH)
/CAN-: D1.1 (A1), J1.6, R10.2, U2.6 (CANL)
/CAN-BUS/Vref: JP1.1 (A), U2.5 (Vref)
/CAN_RX: LED3.1 (K), U2.4 (R)
/CAN_TX: LED2.1 (K), U2.1 (D)
/CHIP_PU: C2.1, C3.1, JP2.1, R1.2, U1.4 (CHIP_PU/RESET)
/Data+: D2.4 (K), J2.A6 (D+), J2.B6 (D+), TP2.1 (1_1), U1.26 (GPIO20/USB_D+/ADC2_CH9)
/Data-: D2.3 (K), J2.A7 (D-), J2.B7 (D-), TP1.1 (1_1), U1.25 (GPIO19/USB_D-/ADC2_CH8)
/Power/BBOUT: C23.1, C24.1, C25.1, TP8.1 (1_1), U4.11 (OUT), U4.13 (OUTS), U5.2 (EN), U5.3 (VIN)
/Power/BIAS: C22.1, U4.5 (BIAS)
/Power/FBIn: R16.2, R17.1, U5.7 (ADJ)
/Power/LX1: L3.1, U4.8 (LX1)
/Power/LX2: L3.2, U4.10 (LX2)
/Power/SEL: R15.1, U4.1 (SEL)
/RXD: TP10.1 (1_1), U1.50 (U0RXD/PROG/GPIO44)
/TXD: LED1.1 (K), R6.1, TP9.1 (1_1)
/detector/V_thresh_A: R28.1, R29.1
/detector/V_thresh_B: R35.1, R36.1
unnamed: C6.1, L1.2, U1.2 (VDD3P3), U1.3 (VDD3P3)
unnamed: C12.2, R19.2
unnamed: C14.1, L2.2, Y1.1
unnamed: C33.1, R26.2
unnamed: C35.1, D4.2 (A), R27.1
unnamed: C41.1, D5.2 (A), R33.1
unnamed: C35.2, R27.2
unnamed: C41.2, R33.2
unnamed: J2.A5 (CC1), R11.1
unnamed: J2.B5 (CC2), R12.2
unnamed: C17.1, JP1.2 (B), R9.2, R10.1
unnamed: LED1.2 (A), R2.2
unnamed: LED2.2 (A), R5.2
unnamed: LED3.2 (A), R18.2
unnamed: LED4.2 (A), R4.1
unnamed: LED5.2 (A), R7.2
unnamed: LED6.2 (A), R13.2
unnamed: Q1.5 (D), R23.2
unnamed: Q1.2 (S), Q1.3 (S), Q1.4 (S), R24.2, R25.2
unnamed: R29.2, R37.2
unnamed: R6.2, U1.49 (U0TXD/PROG/GPIO43)
unnamed: C13.1, U1.53 (XTAL_N), Y1.3
unnamed: L2.1, U1.54 (XTAL_P)
unnamed: R8.1, U2.8 (Rs)
unnamed: R14.2, U3.8 (ST)
unnamed: C19.2, R19.1
unnamed: C32.1, R24.1
unnamed: C30.1, U7.14 (NR)
unnamed: R21.2, R22.1, U7.3 (SENSE/FB)
RBUS_uC_V: J1.3, TP5.1 (1_1), U3.6 (VIN2)
VBUS: D2.2 (K), J2.A4 (VBUS), J2.A9 (VBUS), J2.B4 (VBUS), J2.B9 (VBUS), R13.1, R14.1, U3.3 (VIN1)

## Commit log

2026-06-16 Initialised Repo
    [OPA656UB.step, TLV3201AIDCKT.step, raven-main.kicad_pcb, raven-main.kicad_sch]
2026-06-16 Created detector circuit
    [raven-detector.kicad_sch, raven-main.kicad_sch, raven-power.kicad_sch]
2026-06-16 Added opamp circuits
    [raven-detector.kicad_sch, raven-power.kicad_sch]
2026-06-16 Added LDO Regulator
    [raven-detector.kicad_sch, raven-main.kicad_sch, raven-power.kicad_sch]
2026-06-17 Forgot the changes lol
    [raven-main.kicad_pcb]
2026-06-17 Used the ESP-32 board template to create full board
    [can.kicad_sch, detector.kicad_sch, power.kicad_sch, raven-main.kicad_pcb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]
